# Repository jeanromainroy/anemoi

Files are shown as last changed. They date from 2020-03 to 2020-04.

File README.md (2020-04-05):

# Anemoi : Open Source Ventilator

In the context of the COVID-19 pandemic, the global health system is facing a ventilator shortage. This initiative aims at providing a low-cost and open-source hardware & software design made from ubiquitous components. 

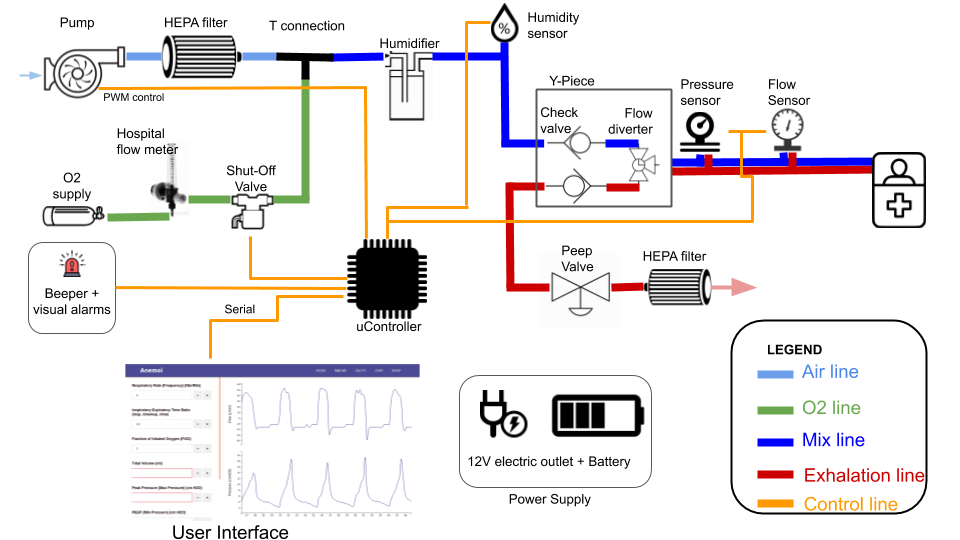
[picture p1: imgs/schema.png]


# Bill of Materials

1. Access to 3d printer and PLA filament. (Our prototype was printed on the Monoprice 3D printer V2)

2. 5/8 inch vinyl tubing (15mm interior diameter)

3. Brass connectors & valves

4. Microcontroller (i.e. arduino) and Computer (i.e. Raspberry Pi)

5. Barometric Pressure (BM280) and Differential (MXP5010) Pressure Sensors

6. Air Pump >50 Watts

7. 12V car battery

# CADs

## Turbine Pump Design

Link to calculator,

		https://inventory.powerzone.com/resources/centrifugal-pump-power-calculator/

## Venturi Valve

The tidal volume delivered to the patient is an essential measurement and thus requires a flow meter. This component is placed in series with the patient's air flow. 
We went with a design with no moving parts that leverages the Venturi effect. The air flows through a constricted section of a pipe. In the direction of the flow, a pressure reading is taken before entering the choke and in the choke. The flow rate can then be obtained with this equation,

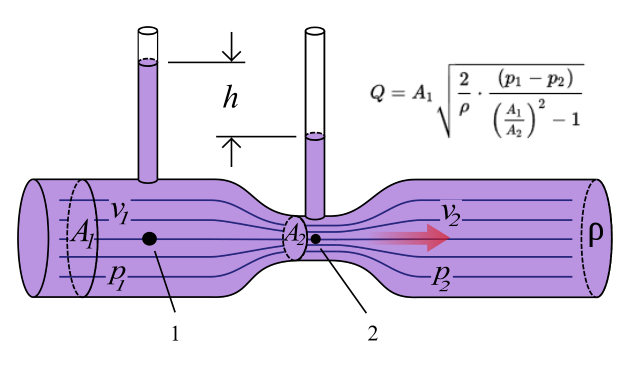
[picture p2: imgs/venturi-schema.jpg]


Our venturi valve is bidirectional to measure the expiratory and inspiratory flow. STL can be found in anemoi/cad/venturi/. 

# Sensors

Sampling frequency for all sensors should be >100ms to prevent performance drops on the UI.

## Pressure Calibration

We connected the water column and the sensor in parallel and we applied a constant pressure using a balloon that we inflate or deflate. 

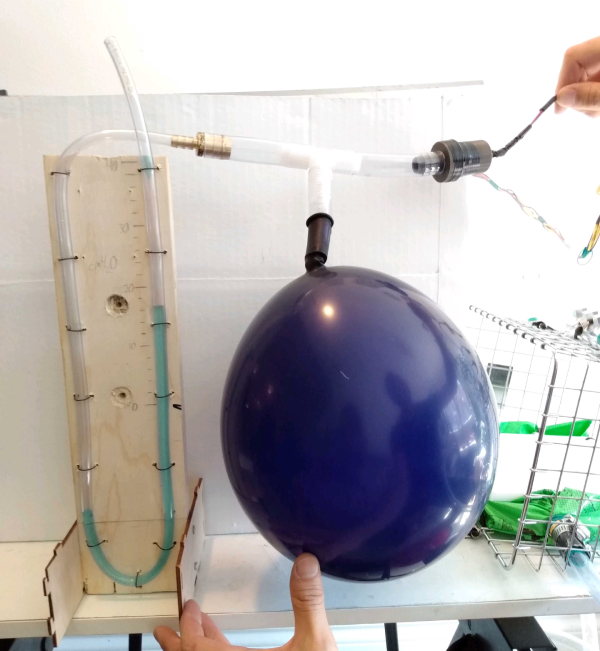
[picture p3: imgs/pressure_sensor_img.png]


We read the values coming from the sensor using the test_sensor.py script. Here are our results,

		Measure Pressure   |   Actual Pressure (cmH2O)
					-4.74   |   0
					15.21   |   20
					17.11   |   22
					18.94   |   24
					20.8   |   26
					22.88   |   28
					24.57   |   30
					26.11   |   32
					27.15   |   34
					26.47   |   36
					27.45   |   38
					7.39   |   11
					6.25   |   10
					5.12   |   9
					4.3   |   8
					0.88   |   4
					2.88   |   6
					-1.22   |   2
					-0.14   |   3
					1.84   |   5
					8.81   |   12
					13.65   |   17
					12.83   |   16
					12.12   |   15
					16.77   |   19

We find the linear regression to find the calibration coffeciants (true_val = c1*sensor_val + static diff between sensors), 

		c1 = 1.14
		c2 = Measured when the machine boots up

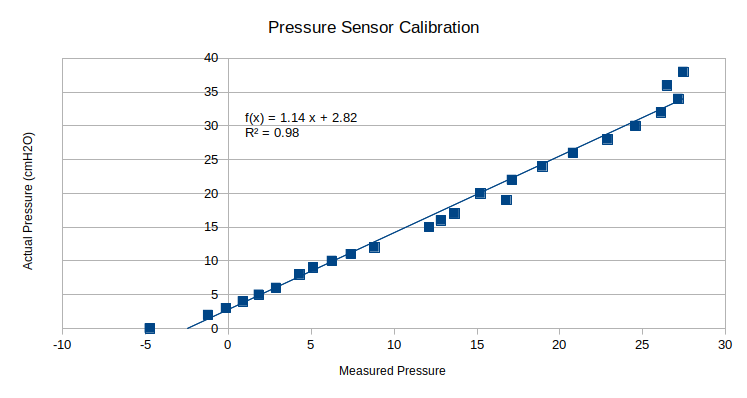
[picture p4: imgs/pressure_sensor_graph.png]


## Flow Calibration

For the flow we use Archimede's Principle stating that if a body is completely submerged the volume of fluid displaced is equal to the volume of the body. We fill a inverted graduated cylinder with water and we place it into a water bucket. We insert the 5/8 tube at the very top of the cylindar (to prevent bubble creation pressure transients).
We integrate the flow sensor reading with the sampling time to get the volume measured and we compare it to the actual volume. The equation relating the flow to the pressure in a venturi valve is squared root. 

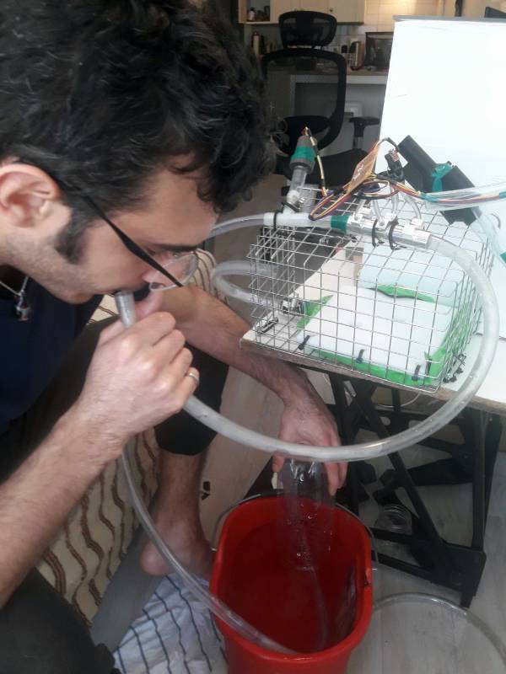
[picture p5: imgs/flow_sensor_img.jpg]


Here are our results,

		Displaced Volume (mL)  |  Square Root of Flow Sensor Rieman Sum
		-------------------------------------------------------------------------------------
						600   |   1.67
						600   |   1.63
						1000   |   2.26
						700   |   1.53
						1000   |   2.26
						900   |   2.32
						650   |   1.53
						1750   |   2.64
						1500   |   3.1
						1200   |   2.31
						1750   |   2.51
						700   |   1.83
						1700   |   2.62
						1500   |   2.36
						1800   |   3.31
						450   |   1.12
						1450   |   2.93
						600   |   1.26
						1000   |   2.28
						450   |   1.16
						700   |   1.64
						650   |   1.61
						650   |   1.22
						650   |   1.4
						600   |   1.2
						1000   |   1.55
						800   |   1.52

We force the y intercept to be at 0,

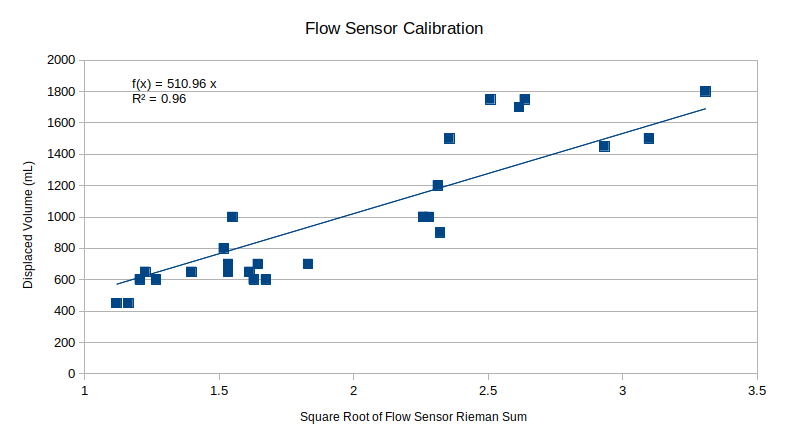
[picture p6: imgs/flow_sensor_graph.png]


# Arduino 

## Mise-en-place

1. Install the following librairies and all dependencies

		Sparkfun BME280 Library

2. Upload the anemoi/arduino/arduino.ino script

# Raspberry Pi

## Installing Raspbian

Format SD Card,

1. Open Gparted

2. Select the SD Card drive

3. Delete all partitions

4. Right click and select format fat32

5. Run all operations

To upload image to SD card,

1. Download the latest Raspbian OS (https://www.raspberrypi.org/downloads/raspbian/)

2. Make sure the sha256 matches the name of the file :

		sha256sum filename.zip

3. Unzip the img

4. We write down the name of the sd card by running,

		sudo fdisk -l

5. We unmount the sd card by running :

		sudo umount /dev/sdb1

6. We write the img to the sd card :

		sudo dd bs=4M if=image_name.img of=/dev/sdb conv=fsync

7. Wait for transfer to end

8. Open /boot/ directory

9. Add file named 'ssh' (no extension)

10. Add file named wpa_supplicant.conf

		country=CA # Your 2-digit country code
		ctrl_interface=DIR=/var/run/wpa_supplicant GROUP=netdev
		network={
			ssid="WIFI_NAME"
			psk="WIFI_PASSWORD"
			key_mgmt=WPA-PSK
		}

11. Eject and Put the SD card in the Pi

12. Wait for Pi to boot and ssh using

		ssh pi@'ip'

		password : raspberry

## Secure the SSH

In order to ssh without a password, only the ssh-key

1. On the pi, generate new ssh keys pair (press enter for all questions) : ssh-keygen

2. Copy your computer's public id to the .ssh/authorized_keys file of the pi
	
		nano ~/.ssh/authorized_keys

## LAMP Stack

To deliver the Anemoi web app, you will need to setup your pi as a LAMP server

  * Make sure your pi is up-to-date

		sudo apt-get update
		sudo apt-get upgrade
		sudo apt-get autoremove

  * A web server
	
		sudo apt-get install apache2 -y

  * A database server
	
		sudo apt-get install mariadb-server -y

  * PHP
		
		sudo apt-get install php-fpm php-mysql -y

## The Firewall

1. Make sure your hostname is set correctly,

		hostnamectl set-hostname --YOUR HOSTNAME--

2. Also add it to hosts file by sudo nano /etc/hosts and adding this under 127.0.0.1 ...
	
		--IP-- --YOUR HOSTNAME--

1. Install ufw

		sudo apt-get install ufw

2. Setup the firewall

		sudo ufw default allow outgoing
		sudo ufw default deny incoming
		sudo ufw allow ssh
		sudo ufw allow 80
		sudo ufw allow 443
		sudo ufw enable
		sudo ufw status

## Mise-en-place

To setup Anemoi you need a couple of additional packages & configurations:

  * All the necessary packages
	
		sudo apt-get install git python3-dev pip3 python3-smbus i2c-tools

  * A lib manager

		sudo apt-get install python3-pip

  * The Python/MySQL connector
		
		sudo python3 -m pip install mysql-connector-python

  * The tmux program to launch multiple command line processes simultaneously
	
		sudo apt-get install tmux

  * Apache Php Interpreter
		
		sudo apt-get install php libapache2-mod-php

  * Make sure the I2C & Serial interface is enabled 

		https://learn.adafruit.com/adafruits-raspberry-pi-lesson-4-gpio-setup/configuring-i2c

  * In raspi-config and the timezone is the one you are in

  * Reboot

## Creating the database

1. Secure MySQL by running

		sudo mysql_secure_installation

1. Log into the MySQL database server

		sudo mysql

2. Create the DB that will be used by anemoi

		CREATE DATABASE anemoi;

3. Create a new user,

		CREATE USER 'username'@'localhost' IDENTIFIED BY 'password';

		GRANT ALL PRIVILEGES ON anemoi.* TO 'username'@'localhost' WITH GRANT OPTION;

		FLUSH PRIVILEGES;

4. Exit and Login with your new credentials

		exit
		mysql -u username -p

5. Select your database

		use anemoi;

6. Create the following tables,	

        CREATE TABLE patient (id int not null auto_increment, name VARCHAR(128), weight_kg int, age int, updated_at TIMESTAMP NOT NULL DEFAULT NOW() ON UPDATE NOW(), created_at TIMESTAMP NOT NULL DEFAULT NOW(), PRIMARY KEY (id));

        CREATE TABLE session (id int not null auto_increment, patient_id int, vac_pc tinyint(1) not null, vac_vc tinyint(1) not null, cpap tinyint(1) not null, bipap tinyint(1) not null, peep int not null, delta_p int, respiration_rate int, inspiration_expiration_ratio float, fio2 int, trigger_level float, tidal_volume int, max_pressure int, updated_at TIMESTAMP NOT NULL DEFAULT NOW() ON UPDATE NOW(), created_at TIMESTAMP NOT NULL DEFAULT NOW(), PRIMARY KEY (id));        

        CREATE TABLE pressure (id int not null auto_increment, value float not null, created_at TIMESTAMP(3) NOT NULL DEFAULT NOW(3), PRIMARY KEY (id));
        
		CREATE TABLE volume (id int not null auto_increment, value float not null, created_at TIMESTAMP(3) NOT NULL DEFAULT NOW(3), PRIMARY KEY (id));

		CREATE TABLE flow (id int not null auto_increment, value float not null, created_at TIMESTAMP(3) NOT NULL DEFAULT NOW(3), PRIMARY KEY (id));

7. Edit config file to start mysql with event_scheduler,

		sudo nano /etc/mysql/mariadb.conf.d/50-server.cnf

8. Add at bottom

		event_scheduler=ON

9. Turn on global scheduler,

		SET GLOBAL event_scheduler = ON;

10. Add pressure cleanup event,

		DELIMITER $$

		CREATE EVENT `Every_60_Minutes_Pressure_Cleanup` 
		ON SCHEDULE EVERY 10 MINUTE 
		ON COMPLETION PRESERVE 
		DO BEGIN delete from pressure where TIMESTAMPDIFF(MINUTE, created_at, now())>60; 
		END;
		$$
		DELIMITER ;

8. Add volume cleanup event,

		DELIMITER $$

		CREATE EVENT `Every_60_Minutes_Volume_Cleanup` 
		ON SCHEDULE EVERY 10 MINUTE 
		ON COMPLETION PRESERVE 
		DO BEGIN delete from volume where TIMESTAMPDIFF(MINUTE, created_at, now())>60; 
		END;
		$$
		DELIMITER ;

9. Make sure the events are saved,

		show events;

10. Check if the event scheduler is on,

		show variables where variable_name='event_scheduler';

## Managing your web folder

1. Change the permissions

		sudo chown -R pi:www-data /var/www/html/

		sudo chmod -R 770 /var/www/html/

## The Anemoi Source Code

1. Clone the Anemoi Repo in /home/

		git clone https://github.com/jeanromainroy/anemoi.git

2. Copy the web files inside your Apache folder

		cp -r ~/anemoi/rpi/web/* /var/www/html/

3. Sensor Packages
		
		sudo pip3 install pyserial bmp280

4. Set your DB credentials in,

		anemoi/rpi/local/db_helper.py

		anemoi/rpi/web/api/config/database.php

## Launching a Daemon on startup

1. Create a new service

        sudo nano /lib/systemd/system/anemoi.service

2. Paste in

        [Unit]
        Description=Anemoi Daemon
		After=mariadb.service

        [Service]
        Type=forking
        User=pi
        ExecStart=/usr/bin/tmux new-session -s anemoi -d 'python3 /home/pi/anemoi/rpi/local/run.py'
        ExecStop=/usr/bin/tmux kill-session -t anemoi
        WorkingDirectory=/home/pi/anemoi/rpi/local/

        [Install]
        WantedBy=multi-user.target

3. Add service

        sudo systemctl enable anemoi.service

4. Reload

        sudo systemctl daemon-reload

5. Restart it,

        sudo systemctl restart anemoi.service

6. Check the status

        systemctl status anemoi.service

## Useful commands

1. Check connected I2C addr

		sudo i2cdetect -y 1

2. Check serial devices

		dmesg | grep tty

3. To share your mouse/keyboard with the pi

  * Install on both machine

		sudo apt-get install x2x

  * Configure the SSH on the server

		nano /etc/ssh/sshd_config

		X11Forwarding yes

  * SSH using,

		ssh -X pi@192.168.XXX.XXX 'x2x -east -to :0'

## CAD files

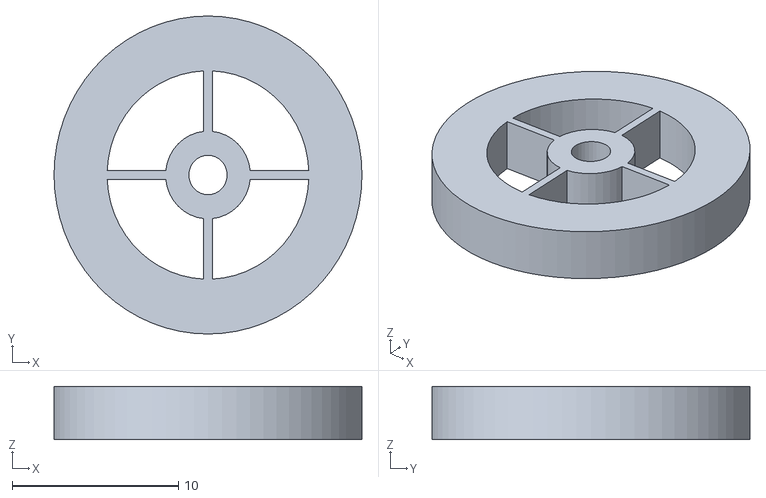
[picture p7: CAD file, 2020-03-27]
cad/check_valve/check_valve_wheel.stl
18.5 x 19.1 x 3.20

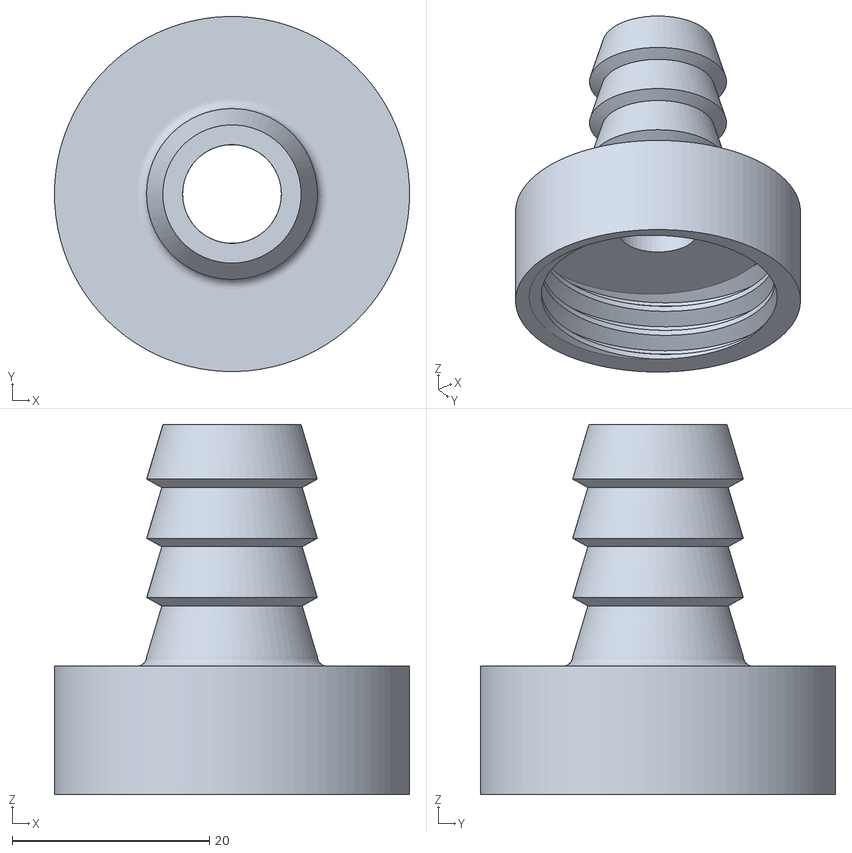
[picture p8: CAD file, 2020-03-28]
cad/sensor/sensor_box_round_top.stl
36.0 x 36.0 x 37.5

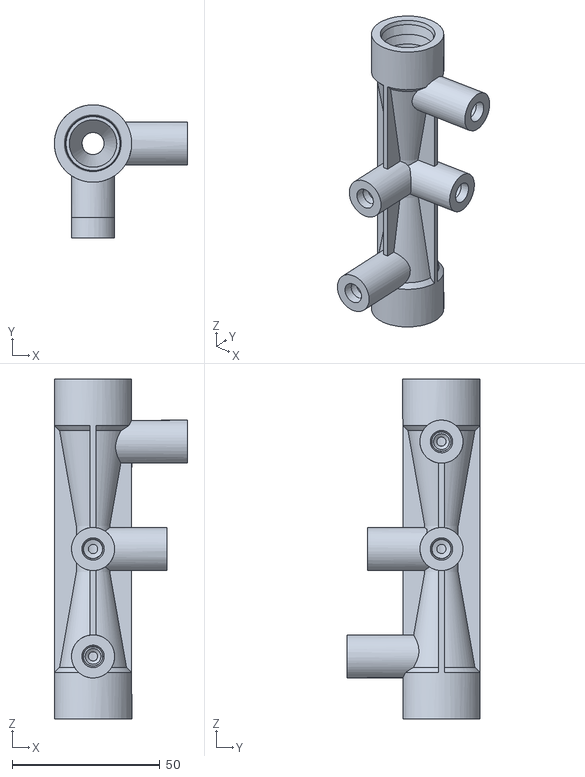
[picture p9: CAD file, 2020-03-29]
cad/venturi/venturi_valve.stl
45.1 x 45.1 x 115.0

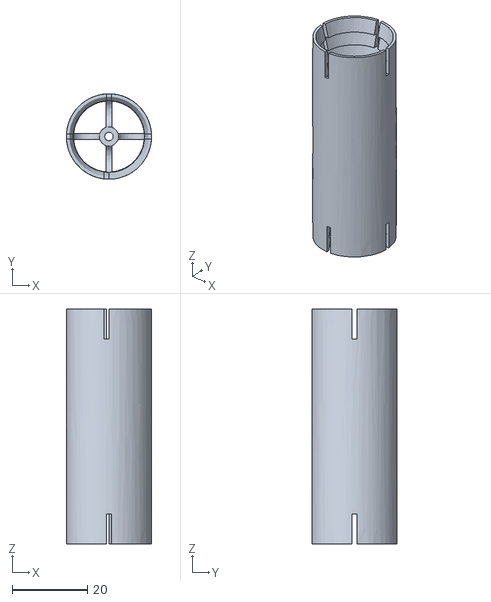
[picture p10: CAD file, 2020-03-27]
cad/check_valve/check_valve_sleeve.stl
22.6 x 22.7 x 62.3

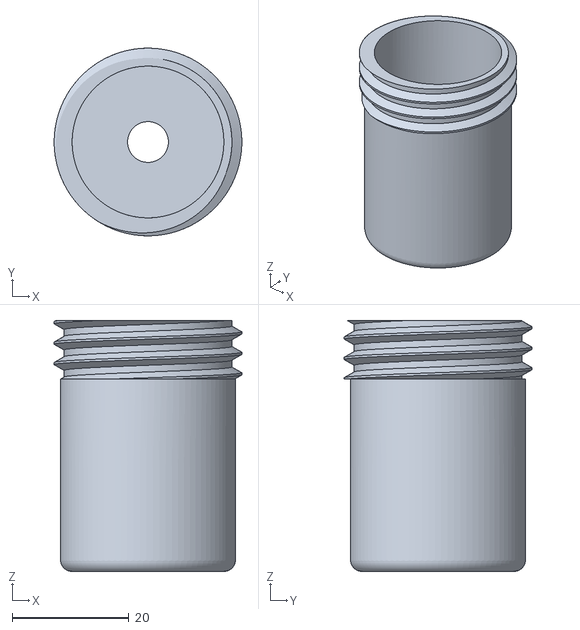
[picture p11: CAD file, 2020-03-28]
cad/sensor/sensor_box_round_bottom.stl
32.2 x 32.2 x 43.0

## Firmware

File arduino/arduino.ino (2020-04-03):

// Libs
#include <Wire.h>
#include <EEPROM.h>
#include "SparkFunBME280.h"

// Allow unsigned char to be written as uchar
typedef unsigned char uchar;

// GENERAL
int LOOP_DELAY = 10; // in ms
int SENSOR_SAMPLE_RATE = 50; // in ms
int counter = 0;

// Get I2C instances of pressure/temp sensors
BME280 bmp_in; //Uses default I2C address 0x77
BME280 bmp_out; //Uses I2C address 0x76 (jumper closed)
float pressure_calib_a = 1.14;
float pressure_calib_b = 0.0;

// The Venturi ADC Pins
#define ADC_CLK 13
#define ADC_CS  12
#define ADC_DI 11
#define ADC_DO 10
float sensor1_calib_b = 8;
float sensor2_calib_b = 11;
float flow_calib_a = 510.96;
float volume = 0.0;

// Pump pins
#define PUMP_OUT 3
#define SOLENOID_OUT 4
int inspiration_addr = 0;
int expiration_addr = 1;
int trigger_addr = 2;
int inspirationTime = -1;
int expirationTime = -1;
int trigger = -1;
int DEFAULT_TRIGGER = 5;
int DEFAULT_INSPIRATION_TIME = 2; // in s
int DEFAULT_EXPIRATION_TIME = 3;  // in s


void setup() {
  
  Serial.begin(9600);
  Serial.println("Initialization Sequence...");

  // BMP
  Wire.begin();
  bmp_out.setI2CAddress(0x77); //The default for the SparkFun Environmental Combo board is 0x77 (jumper open).
  if(bmp_out.beginI2C() == false){
    Serial.println("BMP280 Out connect failed");
    return;  
  }
  bmp_in.setI2CAddress(0x76); //Connect to a second sensor
  if(bmp_in.beginI2C() == false){
    Serial.println("BMP280 In connect failed");
    return;  
  }

  // Set the ADC Pins
  pinMode(ADC_CS, OUTPUT);
  pinMode(ADC_CLK, OUTPUT);
  pinMode(ADC_DI, OUTPUT);
  pinMode(ADC_DO, INPUT); 

  // Set the Pump Pin
  pinMode(PUMP_OUT, OUTPUT); 
  digitalWrite(PUMP_OUT, 0); 
  pinMode(SOLENOID_OUT, OUTPUT); 
  digitalWrite(SOLENOID_OUT, 0); 
  readPumpParams();
  if(inspirationTime <= 0 || expirationTime <= 0 || trigger <= 0){
    updateInspirationTime(DEFAULT_INSPIRATION_TIME);
    updateExpirationTime(DEFAULT_EXPIRATION_TIME);
    updateTrigger(DEFAULT_TRIGGER);
  }
  readPumpParams();
  Serial.print("inspiration:");
  Serial.println(inspirationTime);
  Serial.print("expiration:");
  Serial.println(expirationTime);
  Serial.print("trigger:");
  Serial.println(trigger);

  // Static Pressure Difference 
  delay(2000);
  float pressureAverage = 0.0;
  for(int i = 0; i<20; i++){
    pressureAverage += float(readPressure());  
    delay(50);
  }
  pressure_calib_b = -(float(pressureAverage)/20.0);
  
}


int getADC(short channel){
  // Chip ADC0832

  if(channel != 0 && channel != 1){
    return 0;
  }
  
  pinMode(ADC_DO, OUTPUT); 

  // Bring CS Low
  digitalWrite(ADC_CS, 1); delayMicroseconds(2);
  digitalWrite(ADC_CS, 0);

  // Start Clock
  digitalWrite(ADC_CLK, 0); delayMicroseconds(2);

  // Input MUX Addr
  digitalWrite(ADC_DI, 1); delayMicroseconds(2);
  digitalWrite(ADC_CLK, 1); delayMicroseconds(2);
  digitalWrite(ADC_CLK, 0); delayMicroseconds(2);
  
  digitalWrite(ADC_DI, 1); delayMicroseconds(2);
  digitalWrite(ADC_CLK, 1); delayMicroseconds(2);
  digitalWrite(ADC_CLK, 0); delayMicroseconds(2);
  
  digitalWrite(ADC_DI, channel); delayMicroseconds(2);
  digitalWrite(ADC_CLK, 1); delayMicroseconds(2);
  digitalWrite(ADC_CLK, 0); delayMicroseconds(2);

  // Read 8 bit ADC
  uchar dat=0;
  for(short i=0; i<8; i++){
    digitalWrite(ADC_CLK, 1); delayMicroseconds(2);
    digitalWrite(ADC_CLK, 0); delayMicroseconds(2);
    
    pinMode(ADC_DO, INPUT);
    dat=dat<<1 | digitalRead(ADC_DO);
  }

  // Convert to int
  int value = 0;
  for(unsigned int i=0; i<8; i++) {
    if(bitRead(dat,i) == 1){
      value += pow(2,i);
    }    
  }

  return value;  
}


float readPressure(){

  // Get the pressure diff between the two sensors in hPa
  float pressure_in = bmp_in.readFloatPressure();
  float pressure_out = bmp_out.readFloatPressure();
  
  float pressureDiff = (pressure_in - pressure_out)*0.01;

  // Convert to cm h2o
  pressureDiff = pressureDiff*1.0197;

  // Use calibration
  pressureDiff = pressure_calib_a*pressureDiff + pressure_calib_b;

  // print
  return pressureDiff;
}

void readTemp(){

  // Read in *C
  float temp = bmp_in.readTempC();
  
  // Print
  Serial.print("temperature:");
  Serial.println(temp, 2);  // 2 decimals  
}

float readFlow(){

  // Read differential pressures
  int diffPressure1 = int(getADC(0)) - sensor1_calib_b;    // expiration
  int diffPressure2 = int(getADC(1)) - sensor2_calib_b;    // inspiration

  // We are going to take the sqrt, make sure its positive
  if(diffPressure1 < 0){
    diffPressure1 = 0;
  }
  if(diffPressure2 < 0){
    diffPressure2 = 0;  
  }

  // Convert to Flow with Venturi Equation
  float flow = 0.0;
  if(diffPressure1 > diffPressure2){
    flow = -flow_calib_a*sqrt(diffPressure1);
  }else{   
    flow = flow_calib_a*sqrt(diffPressure2);
  }
  
  // Print
//  Serial.print("flow_expi:");
//  Serial.println(diffPressure1);  
//  Serial.print("flow_inspi:");
//  Serial.println(diffPressure2);
//  Serial.print("flow:");
//  Serial.println(flow,2);  

  return flow;
}

float readVolume(){

  // read flow
  float flowVal = float(readFlow());

  // accumulate
  if(flowVal >= 0.0){
    volume += flowVal*(float(SENSOR_SAMPLE_RATE)/1000.0);
  }

  return volume;   
}

void updateInspirationTime(short inspirTime){
  EEPROM.update(inspiration_addr, inspirTime);
  inspirationTime = inspirTime;
  Serial.print("Updated Inspiration Time to ");
  Serial.print(inspirationTime);
  Serial.println("s");
}

void updateExpirationTime(short expirTime){
  EEPROM.update(expiration_addr, expirTime);
  expirationTime = expirTime;
  Serial.println("Updated Expiration Time to ");
  Serial.print(expirationTime);
  Serial.println("s");
}

void updateTrigger(short trig){
  EEPROM.update(trigger_addr, trig);
  trigger = trig;
  Serial.println("Updated Trigger to ");
  Serial.print(trigger);
  Serial.println(" cmH2O");
}

void readPumpParams(){
  inspirationTime = EEPROM.read(inspiration_addr);
  expirationTime = EEPROM.read(expiration_addr);
  trigger = EEPROM.read(trigger_addr);
}


String splitString(String data, char separator, int index){
  int found = 0;
  int strIndex[] = { 0, -1 };
  int maxIndex = data.length() - 1;
  
  for (int i = 0; i <= maxIndex && found <= index; i++) {
    if (data.charAt(i) == separator || i == maxIndex) {
      found++;
      strIndex[0] = strIndex[1] + 1;
      strIndex[1] = (i == maxIndex) ? i+1 : i;
    }
  }
  return found > index ? data.substring(strIndex[0], strIndex[1]) : "";
}


boolean isValidNumber(String str){
  boolean isNum=false;
  for(byte i=0;i<str.length();i++){
    isNum = isDigit(str.charAt(i)) || str.charAt(i) == '+' || str.charAt(i) == '.' || str.charAt(i) == '-';
    if(!isNum) return false;
  }
  return isNum;
}

void loop() {

  // Increment Counter
  counter += 1;

  // Run Pump
  if(counter <= (expirationTime*1000)/LOOP_DELAY){
    digitalWrite(PUMP_OUT, 1);
    digitalWrite(SOLENOID_OUT, 1);
    volume = 0;
  }else if(counter > (expirationTime*1000)/LOOP_DELAY && counter < ((expirationTime*1000)/LOOP_DELAY) + ((inspirationTime*1000)/LOOP_DELAY)){
    digitalWrite(PUMP_OUT, 0);
    digitalWrite(SOLENOID_OUT, 0);
  }else{
    counter = 0;  
  }

  // Read Sensors
  if(counter % (SENSOR_SAMPLE_RATE/LOOP_DELAY) == 0){

    // Pressure
    float pressureVal = float(readPressure());
    Serial.print("pressure:");
    Serial.println(pressureVal, 2);  // 2 decimals

    // Volume
    float volumeVal = float(readVolume());
    Serial.print("volume:");
    Serial.println(volumeVal,2);  

    // Check for trigger
    if(pressureVal <= -trigger){
        digitalWrite(PUMP_OUT, 0);
        digitalWrite(SOLENOID_OUT, 0);     
        counter = 0;
        volume = 0;
    }
  }

  // Read Serial
  while(Serial.available()) {
    
    // read the incoming data as string
    String received = Serial.readStringUntil(';');

    // check
    if(received == NULL || received.length() == 0){
      continue;
    }

    // prompt master
    Serial.print("Arduino received : ");
    Serial.println(received);
    
    // Convert to char array
    String key = splitString(received, ':', 0);
    String val = splitString(received, ':', 1);

    // check
    if(key != NULL && val != NULL && key.length() > 0 && val.length() > 0){

      // remove leading & trailing whitespaces
      key.trim();
      val.trim();

      // check if val is numeric
      if(!isValidNumber(val)){
        continue;
      }

      // convert to int
      int intVal = val.toInt();
      
      if(key.equals("inspiration_time")){
        updateInspirationTime(intVal);
        
      }else if(key.equals("expiration_time")){
        updateExpirationTime(intVal);
        
      }else if(key.equals("trigger")){
        updateTrigger(intVal);
      }
    }
  }

  // wait
  delay(LOOP_DELAY);
}

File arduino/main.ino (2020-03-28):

// Libs
#include <Adafruit_BMP280.h>
#include <EEPROM.h>

// Allow unsigned char to be written as uchar
typedef unsigned char uchar;

// GENERAL
int LOOP_DELAY = 10; // in ms
int SENSOR_SAMPLE_RATE = 200; // in ms
int counter = 0;

// Get I2C instances of pressure/temp sensors
Adafruit_BMP280 bmp_in;
Adafruit_BMP280 bmp_out; 

// Set the ADC pins
#define ADC_CLK 13
#define ADC_CS  12
#define ADC_DI 11
#define ADC_DO 10

// Pump pins
#define PUMP_OUT 3
int inspiration_addr = 0;
int expiration_addr = 1;
int inspirationTime = -1;
int expirationTime = -1;
int DEFAULT_INSPIRATION_TIME = 2; // in s
int DEFAULT_EXPIRATION_TIME = 3;  // in s


void setup() {
  
  Serial.begin(9600);

  Serial.println("Initialization Sequence...");
  
  if (!bmp_in.begin(0x76)) {
    Serial.println(F("Could not find a valid BMP280_1 sensor, check wiring!"));
    while (1);
  }

  if(!bmp_out.begin(0x77)){
    Serial.println(F("Could not find a valid BMP280_2 sensor, check wiring!"));
    while (1);    
  }

  /* Default settings from datasheet. */
  bmp_in.setSampling(Adafruit_BMP280::MODE_NORMAL,     /* Operating Mode. */
                  Adafruit_BMP280::SAMPLING_X2,     /* Temp. oversampling */
                  Adafruit_BMP280::SAMPLING_X16,    /* Pressure oversampling */
                  Adafruit_BMP280::FILTER_X16,      /* Filtering. */
                  Adafruit_BMP280::STANDBY_MS_500); /* Standby time. */

  bmp_out.setSampling(Adafruit_BMP280::MODE_NORMAL,     /* Operating Mode. */
                  Adafruit_BMP280::SAMPLING_X2,     /* Temp. oversampling */
                  Adafruit_BMP280::SAMPLING_X16,    /* Pressure oversampling */
                  Adafruit_BMP280::FILTER_X16,      /* Filtering. */
                  Adafruit_BMP280::STANDBY_MS_500); /* Standby time. */

  // Set the ADC Pins
  pinMode(ADC_CS, OUTPUT);
  pinMode(ADC_CLK, OUTPUT);
  pinMode(ADC_DI, OUTPUT);
  pinMode(ADC_DO, INPUT); 

  // Set the Pump Pin
  pinMode(PUMP_OUT, OUTPUT);  
  readPumpParams();
  if(inspirationTime <= 0 || expirationTime <= 0){
    updateInspirationTime(DEFAULT_INSPIRATION_TIME);
    updateExpirationTime(DEFAULT_EXPIRATION_TIME);
  }
  readPumpParams();
  Serial.print("inspiration:");
  Serial.println(inspirationTime);
  Serial.print("expiration:");
  Serial.println(expirationTime);
}


uchar getADC(short channel){
  // Chip ADC0832

  if(channel != 0 && channel != 1){
    return 0;
  }
  
  pinMode(ADC_DO, OUTPUT); 

  // Bring CS Low
  digitalWrite(ADC_CS, 1); delayMicroseconds(2);
  digitalWrite(ADC_CS, 0);

  // Start Clock
  digitalWrite(ADC_CLK, 0); delayMicroseconds(2);

  // Input MUX Addr
  digitalWrite(ADC_DI, 1); delayMicroseconds(2);
  digitalWrite(ADC_CLK, 1); delayMicroseconds(2);
  digitalWrite(ADC_CLK, 0); delayMicroseconds(2);
  
  digitalWrite(ADC_DI, 1); delayMicroseconds(2);
  digitalWrite(ADC_CLK, 1); delayMicroseconds(2);
  digitalWrite(ADC_CLK, 0); delayMicroseconds(2);
  
  digitalWrite(ADC_DI, channel); delayMicroseconds(2);
  digitalWrite(ADC_CLK, 1); delayMicroseconds(2);
  digitalWrite(ADC_CLK, 0); delayMicroseconds(2);

  // Read 8 bit ADC
  uchar dat=0;
  for(short i=0; i<8; i++){
    digitalWrite(ADC_CLK, 1); delayMicroseconds(2);
    digitalWrite(ADC_CLK, 0); delayMicroseconds(2);
    
    pinMode(ADC_DO, INPUT);
    dat=dat<<1 | digitalRead(ADC_DO);
  }
  
  return dat;  
}

void readPressure(){

  // Get the pressure diff between the two sensors in hPa
  float pressureDiff = (bmp_in.readPressure() - bmp_out.readPressure())*0.01;

  // Convert to cm h2o
  pressureDiff = pressureDiff*1.0197;

  // Print
  Serial.print("pressure:");
  Serial.println(pressureDiff, 2);  // 2 decimals
}

void readTemp(){

  // Read in *C
  float temp = bmp_in.readTemperature();
  
  // Print
  Serial.print("temperature:");
  Serial.println(temp, 2);  // 2 decimals  
}

void readFlow(){

  uchar flow1 = getADC(0);
  uchar flow2 = getADC(1);
  
  // Print
  Serial.print("flow1:");
  Serial.println(flow1);  
  Serial.print("flow2:");
  Serial.println(flow2);  
}

void updateInspirationTime(short inspirTime){
  EEPROM.write(inspiration_addr, inspirTime);
}

void updateExpirationTime(short expirTime){
  EEPROM.write(expiration_addr, expirTime);  
}

void readPumpParams(){
  inspirationTime = EEPROM.read(inspiration_addr);
  expirationTime = EEPROM.read(expiration_addr);
}


void loop() {

  counter += 1;

  if(counter < (expirationTime*1000)/LOOP_DELAY){
    digitalWrite(PUMP_OUT, 0);
  }else if(counter >= (expirationTime*1000)/LOOP_DELAY && counter < ((expirationTime*1000)/LOOP_DELAY) + ((inspirationTime*1000)/LOOP_DELAY)){
    digitalWrite(PUMP_OUT, 1);
  }else if(counter >= ((expirationTime*1000)/LOOP_DELAY) + ((inspirationTime*1000)/LOOP_DELAY)){
    counter = 0;    
  }
  
  if(counter % (SENSOR_SAMPLE_RATE/LOOP_DELAY) == 0){
    readPressure();
    readFlow();
  }

  // wait
  delay(LOOP_DELAY);
}

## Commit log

2020-03-23 fixed mysql socket pre
2020-03-23 pressure graph
2020-03-24 incr/decr buttons
    [Bottom_threaded.stl, Top_Screwed.stl, Top_threaded.stl]
2020-03-25 pressure sensor
2020-03-26 arduino template
    [Bottom_threaded.stl, Top_Screwed.stl, Top_threaded.stl, bottom.stl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]
2020-03-26 nbr of points dynamic
    [mini_check_valve_sleeve.stl]
2020-03-26 i2c disconnect exception
    [mini_check_valve_sleeve.stl]
2020-03-26 check valve wheel
    [roue_valve.stl]
2020-03-27 flow sensor
    [check_valve_sleeve.stl, check_valve_wheel.stl, mini_check_valve_sleeve.stl, roue_valve.stl]
2020-03-27 flow api
2020-03-28 synced lines
    [bottom.stl, middle.stl, sensor_box_round_bottom.stl, sensor_box_round_top.stl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]
2020-03-28 moved to arduino
2020-03-29 venturi valve
    [venturi_valve.stl]
2020-03-29 flow in right units
2020-03-31 test sensors
2020-03-31 pressure calibration
2020-03-31 changed flow to volume
